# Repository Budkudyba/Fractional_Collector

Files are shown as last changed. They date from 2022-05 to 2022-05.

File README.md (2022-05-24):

# Fractional_Collector
## A Device that collects samples at interval.
A novel spin on fractional collection...Maintaining a Constant volume of the sampled media.  
  
The controller uses the Ramps 1.4 board and Arduino Mega commonly used in 3D printers. 
DRV8825 Stepper Drivers were used.  
  
The sampler takes samples based upon polling an added RTC (real-time clock).  
  
The sampler has two attached parastaltic pumps with stepper motors and a sample tray which is also powered by a stepper motor.  
The sample tray has room for 64 small eppendorf (1.5 mL).  
  
Here's a version of the sampler to show the basic form:  
fractional_collector_FINAL_SHOW
  
https://a360.co/2QkRquD

Libraries used:  
https://github.com/adafruit/RTClib  
https://github.com/olikraus/u8g2  
https://github.com/laurb9/StepperDriver

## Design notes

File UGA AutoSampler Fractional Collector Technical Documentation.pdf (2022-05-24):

## Constant Volume Fractional Collector 1.0

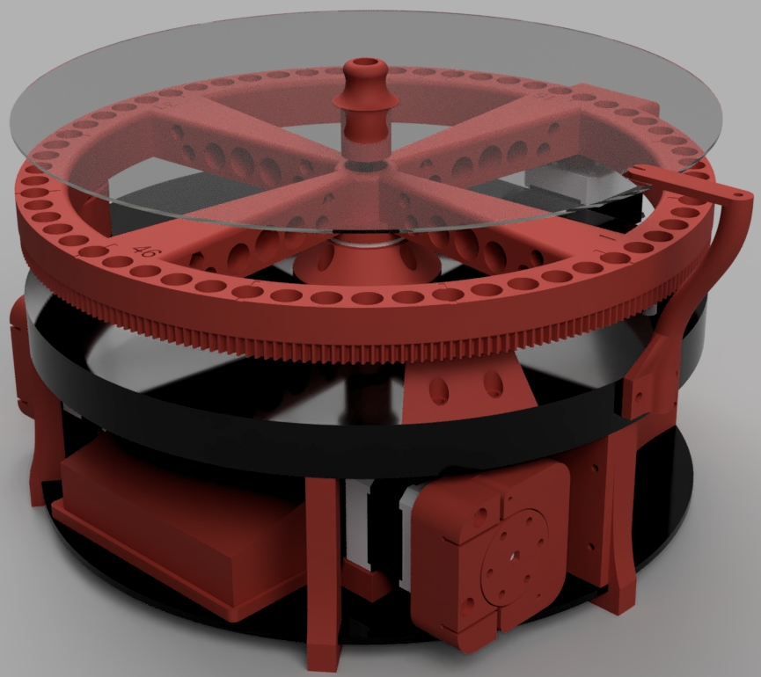
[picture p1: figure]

By: Paul Kudyba, III
8/30/18

### General Operation

- Description of Operation
- This device is used to sample at user given intervals from a blood bag or other sample container while keeping constant volume in the sample container. It can also be used to fill or empty a container to a set amount. Before each sample it will purge the dead volume from the sample tubing ensuring that samples taken are discrete. The controller interface is an LCD display with rotary encoder and push button for ease of operation.
- Powering the device
- The device is powered by a 12v power brick. USB is provided for updating the firmware only.
- Loading sample tubes
- With the top cover removed, place the tubes with the top facing outwards. If desired, you can alternate whether the top is facing inside or outside to help keep track of purge and sample tubes. If the mast is blocking the tube you would like to load/unload, then use the Tray Advance function.
- Purge and Sample
- The device will first purge and then sample. Therefore, each sample will be in an even numbered location.
- Menu Options
- Start
■ When all options are set. Depress the Knob to start the sampling operation. There is a delay of 15 seconds to provide time if an error in setup is made.
- Reset Total Samples
■ This is used to reset the number of samples back to zero. This will set both run and total sample counts back to zero. When used the machine will rehome and start from the first sample tray effectively starting over.
- Tray Advance
■ When loading/unloading, you may need to retrieve an eppendorf that is currently under the mast or move the tray to make it easier to load/unload. This moves the tray one position.
■ If used during a pause. It will resume where it left off after it rehomes. (Ex after taking 5 samples, you pause and advance the tray. When you resume it will resume taking sample 6 where sample 6 is normally taken.)
- Fill Bag
■ This fills the bag to a set amount. This can be changed with Set Bag Volume.
- Empty Bag
■ This empties the bag the amount set. This can be changed with Set Bag Volume.

- Set Cycle Interval
■ This sets how often samples are to be taken
- Set Sample Volume
■ This sets how much you would like to sample
- Set Purge Volume
■ This sets how much is needed to clear the dead volume within the tubing, needle tip, and IV spike. (0.5mL being plenty for up to 4ft of tubing)
- Set Bag Volume
■ This set how much will be pumped in the fill bag and empty bag function.
- Set Sample Limit
■ This is used to take a set number of samples and then pause. The number is taken from the total samples taken number not the run number. (ex. for 10 samples per run this needs to be set to 10 for run one, then 20 and then 30 in between each run)
- Calibrate Input Pump
■ This runs a calibration routine. It will pump a set amount and ask for a measurement of this amount to calculate the difference and adjust for any deviation. For the input pump it is 90mL. This will take a few minutes to pump.
- Calibrate Sample Pump
■ This runs a calibration routine. It will pump a set amount and ask for a measurement of this amount to calculate the difference and adjust for any deviation. For the input pump it is 8mL. This will take a few minutes to pump.
- Set Clock Time
■ This allows for setting/adjusting of the clock.
- Stats
■ This will display total cycles run by each pump. This will help indicate current wear of the tubing. This is not persistent across power cycles. To reset simply power cycle the machine.

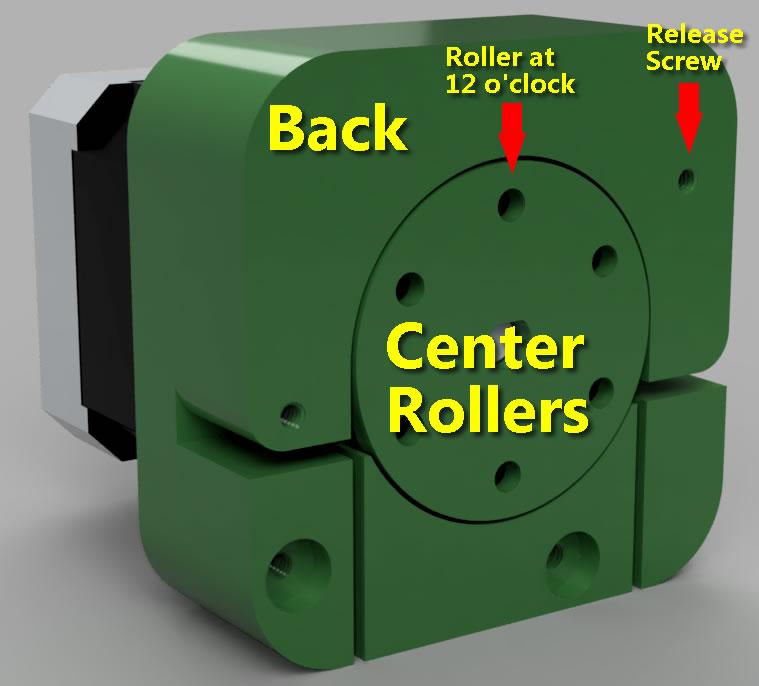
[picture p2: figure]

Changing the tubing

1. Find the release screw, and unscrew until the back of the pump can rotate out.
2. Remove and replace the tubing with the same size tubing required.
3. Close the back of the pump making sure the tubing is pulled taught and in the center of the channel. This is critical for the smaller sample pump.
4. While holding the pump closed so that the back is flat with the rest of the pump, tighten the screw. Do not continue to tighten if the screw is not seating in place.
5. Ensure that the hose is properly seated by:
a. On the larger (Input) pump pull on one side of the hose until you can see that it is drawing the other side into the pump.
b. On the smaller pump, pull until taught on both sides. Do not pull too hard or you may damage the small tubing.
6. Rotate the center rollers counter-clockwise until one of the rollers is at the twelve o’clock position. This ensures that you’ve not pinched the hose or have a bind in the pump. Having a roller at the 12 o’clock position ensures that no fluid will pass through the pump while at rest. This is where the roller “pinches” the hose.
7. Your pump is now ready for calibration.

### Troubleshooting

- Under normal operation the pumps and tray will be powered off when not active and thus able to be moved manually. If you bump the tray in between sampling you can simply pause and use the tray advance function. It will rehome and continue from where you left off when you resume sampling.
- If the pumps are not at the 12 o’clock position then the pumps may not function as intended.
- To first prime the input pump you can run the Fill Bag routine. You can set the volume you wish to prime with Set Bag Volume. When the pump is primed you can unplug the machine, but will lose any calibrations! or wait for the routine to finish. Priming the sample pump is unnecessary due to the purge function.
- Calibration is currently stored in volatile memory and therefore is lost when power is cut. If the device loses power then it must be calibrated before samping is resumed.
- If the sample limit (Set Sample Limit) is reached then it must be increased or the total samples reset (Reset Total Samples) otherwise the device will just pause again when told to sample due to its limit being reached.

### Silicone tubing Specifications

Sample Pump: 1.5mm OD, 0.5mm ID Input Pump: 4mm OD, 2mm ID

### Needle tip

Blunt 22 gauge at least 0.5in

### Eppendorf Specifications

1.5mL capacity micro centrifuge tubes

### Default Pump Calibrations

Input pump: 39.3095uL per ⅙ rotation sample pump: 2.20239uL per ⅙ rotation

### BOM Link

https://docs.google.com/spreadsheets/d/1MYYxMttSNWKxErDTZDmeEtySJJO_4VXljwuw_aIDuVE/edit?usp=sharing (https://docs.google.com/spreadsheets/d/1MYYxMttSNWKxErDTZDmeEtySJJO_4VXljwuw_aIDuVE/edit?usp=sharing)

### Firmware Code

https://drive.google.com/file/d/1aw9PEniRBlol2bpzdIY7CREgvx_vjx7f/view?usp=sharing

### STL Files (Pumps and Fractional Collector)

https://drive.google.com/file/d/1LXug6uyhkMV_s8yWWPx-mD0cbzlMRUWw/view?usp=sharing

### STL Files (IV Bag Adapters)

https://drive.google.com/file/d/1MMP1FGXNb9iqxeFYemUpdmFmI8zt_3Np/view?usp=sharing

### Assembly Drawings

https://drive.google.com/file/d/1KUkplYkBTQmoT0WgEx9ByRFT1yGoU6eH/view?usp=sharing

### Dead Volume Calculations

https://docs.google.com/spreadsheets/d/1AhHszSA9m7Kb7Sqf_vfh5iA0tXgWszb41xrvR_gTXpM/edit?usp=sharing (https://docs.google.com/spreadsheets/d/1AhHszSA9m7Kb7Sqf_vfh5iA0tXgWszb41xrvR_gTXpM/edit?usp=sharing)

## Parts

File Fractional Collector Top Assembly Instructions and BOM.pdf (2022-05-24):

# Fractional Collector Top Assembly Instructions and BOM

STL Link:
https://drive.google.com/file/d/1_8GxYKEukr-SobEUdoyhmjx0G93fVQS1/view?usp=sharing

# BOM

- 3D printed top in polycarbonate or other material able to be autoclaved.
- 22 gauge syringe needle 1½” (only for 2 port tops)
- ⅛” 304 Stainless Steel Tubing Precision (0.125" OD, 0.015" Wall Thickness)
- https://www.mcmaster.com/6100K491/
- #117 Hi-temp Silicone o-ring (red)

# Assembly Instructions

1. Cut 1/8" stainless tube to 1.5" long sections (dremel)
a. Deburr and polish (3/16" drill bit fits the ID)
2. Remove the needles point if hypodermic (dremel)
a. Cut needle tip from luer lock (dremel)
b. Very carefully deburr and polish (0.4mm drill bit fits the ID)
3. Drill top to size. (1/8" drill bit) (press fit)
4. Drill top to size. (0.8mm drill bit) (loose fit) (if required)
a. Press fit stainless tube into top till flush with thread bottom
b. Fit needle into top till flush with bottom (if required)
5. Prep 2 part epoxy (1 hr set is recommended)
a. Line epoxy around the needle and stainless tube
b. Ensure that it covers at least ⅛” up side of needle and stainless tube and ⅛” surrounding top to ensure good bond and proper seal
6. After allowing 24 hrs to cure place o-ring and it is ready for use

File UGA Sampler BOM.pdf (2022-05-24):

Constant Volume Fractional Collector BOM

Name of Part | Number | Price | Origin | Discription | Link | Price Per Unit
Ramps 1.4 Kit | 1 | $29.99 Ebay | https://www.ebay.com/itm/3D-Printer-Kit-Ramps-1-4-Mega2560-DRV8825-12864-LCD-for-Arduino-RepRap-USA/392055803590?ssPageName=STRK%3AMEBIDX%3AIT&_trksid=p2057872.m2749.l2649
Nema 17 Stepper Motors | 3 | $38.97 Amazon | https://www.amazon.com/gp/product/B00PNEQI7W/ref=oh_aui_search_detailpage?ie=UTF8&psc=1 $12.99
DS3231 Precision RTC | 1 | $2.35 Ebay | Real Time Clock | https://www.ebay.com/itm/DS3231-AT24C32-IIC-Precision-Real-Time-Clock-RTC-Memory-Module-for-Arduino/121936579559?ssPageName=STRK%3AMEBIDX%3AIT&_trksid=p2057872.m2749.l2649
LIR2032 Battery | 1 | $7.08 Ebay
| | | | DO NOT USE
CR2032 | https://www.ebay.com/itm/8-X-LIR2032-CR2032-2032-Top-Quality-Bulk-3-6V-Rechargeable-Lithium-Battery/142570686578?ssPageName=STRK%3AMEBIDX%3AIT&_trksid=p2057872.m2749.l2649
#4-40 Machine Screw x 3/4" | 8 | $0.47 Fastenal | https://www.fastenal.com/products/details/72490 $0.06

#4-40 Machine Screw x 1/2" | 20 | $0.60 Fastenal | https://www.fastenal.com/products/details/28655 $0.03

#4-40 Machine Screw x 1/4" | 8 | $0.24 Fastenal | https://www.fastenal.com/products/details/28631 $0.03

#4-40 Nut | 15 | $0.00 Fastenal

#6 Woodscrew Pan Head x 3/4" | 18 | $1.25 | https://www.fastenal.com/products/details/30562 $0.07

#10-24 Machine Screw x 1/2" | 1 | $0.04 Fastenal | https://www.fastenal.com/products/details/28957 $0.04

M3-0.5 x 6mm Machine Screw | 12 | $0.59 Fastenal
| | | | used to attach
stepper motors | https://www.fastenal.com/products/details/QM2510006A20000 $0.05
M3-0.5 x 10mm Machine Screw | 2 | $0.10 Fastenal | to secure endstop | https://www.fastenal.com/products/details/QM2510010A20000 $0.05
M5-0.8 x 50mm Machine Screw | 1 | $0.50 Fastenal | https://www.fastenal.com/products/details/QM2540050A20000 $0.50
M5-0.8 Nut | 2 | $0.24 Fastenal | https://www.fastenal.com/products/details/MN2540000A40000 0.12
Silicone Tubing 0.5mm x 1.5mm | >2ft | $11.26 Ebay | https://www.ebay.com/itm/ID-0-5x-OD-1-5mm-Silicone-Tubing-Food-Grade-Translucent-Rubber-Hose-Beer-Pipe-5M/302738630251?ssPageName=STRK%3AMEBIDX%3AIT&_trksid=p2057872.m2749.l2649
Silicone Tubing 2mm x 4mm | >2ft | $6.30 Amazon | https://www.amazon.com/gp/product/B01C3GCZTM/ref=oh_aui_detailpage_o09_s00?ie=UTF8&psc=1
1/8" x 3/4" Steel Dowel Pins x100 | 1 | $10.25 Ebay | 6 per pump | https://www.ebay.com/itm/1-8-X-3-4-Dowel-Pins-Hardened-Ground-1144-Grade-Steel-USA-Qty-100/173311906972?ssPageName=STRK%3AMEBIDX%3AIT&_trksid=p2057872.m2749.l2649
1kg PLA Filament | 1 | $22.99 Amazon | https://www.amazon.com/gp/product/B00J0EE1D4/ref=od_aui_detailpages00?ie=UTF8&psc=1
3/4" MDF | 1 | $7.71 Home Depot | https://www.homedepot.com/p/3-4-in-x-2-ft-x-2-ft-Medium-Density-Fiber-Board-1508111/205881912
1/4" Smooth Wood Paneling | 1 | $7.75 Home Depot | https://www.homedepot.com/p/Columbia-Forest-Products-1-4-in-x-2-ft-x-2-ft-PureBond-Pre-Primed-Poplar-Plywood-Project-Panel-Free-Custom-Cut-Available-3141/204940167?cm_mmc=Shopping%7CG%7CBase%7CD21%7C21-3_DIMENSIONAL_LUMBER%7CGeneric%7CPLA%7c71700000032182435%7c58700003832328702%7c92700036298154525&gclid=CjwKCAjwq57cBRBYEiwAdpx0vQEbKH0jGUsqRD1It-POHEHfkeOmMzfJ6ZSWmqfee-WHdmYR4G_bkhoCCkIQAvD_BwE&gclsrc=aw.ds&dclid=CKme2Papld0CFTbI4wcd2UMKgg
625ZZ | 2 | $1.40 Amazon | 5mm ID 16mm OD https://www.amazon.com/Bearing-Shielded-Miniature-Bearings-Skateboard/dp/B07DZDZNJM/ref=sr_1_2_sspa?ie=UTF8&qid=1535650890&sr=8-2-spons&keywords=625zz+bearing&psc=1 $0.70
Nylon Washer 1.25" x 0.38" x 0.125" | 2 | $1.90 Ace hardware | $0.95
Blunt 22g Needle | 1 | $0.38 Tractor Supply | Blunted with dremel https://www.tractorsupply.com/tsc/product/producers-pride-disposable-needle-22g-x-1-pack-of-6?cm_vc=-10005 $0.38
Total: | $151.98

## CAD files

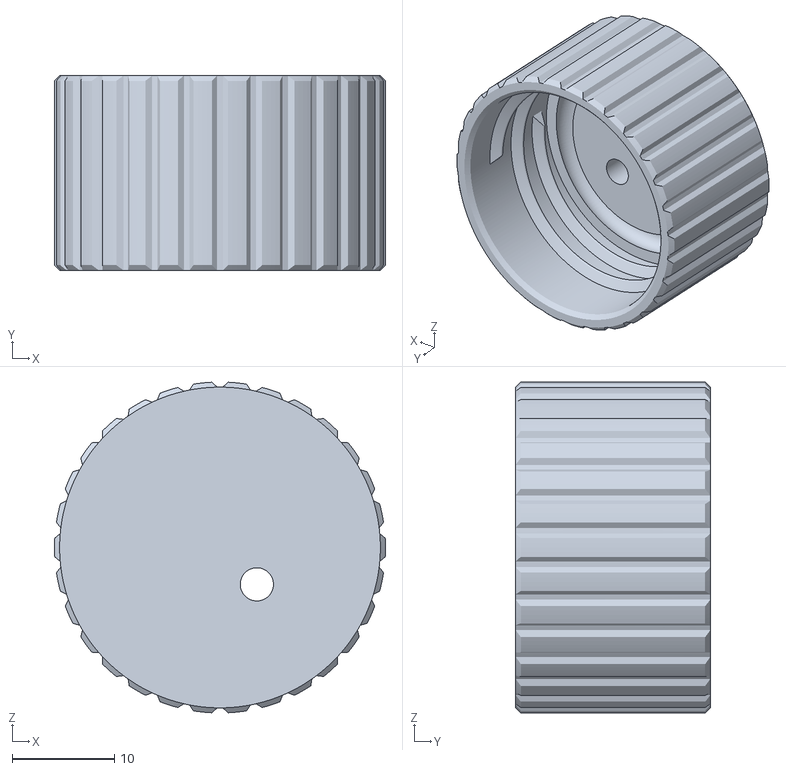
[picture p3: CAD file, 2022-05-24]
STL Files/Bottle Cap Flask FDM with barbs oring v5/Bottle Cap Flask FDM with barbs oring v5 Single.stl
32.3 x 19.0 x 32.3

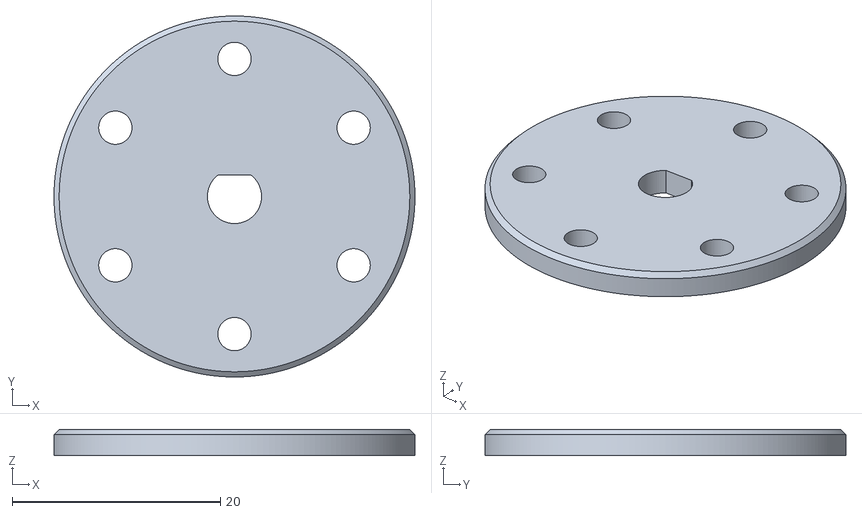
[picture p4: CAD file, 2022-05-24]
STL Files/input pump/roller_base.stl
34.7 x 34.7 x 2.50

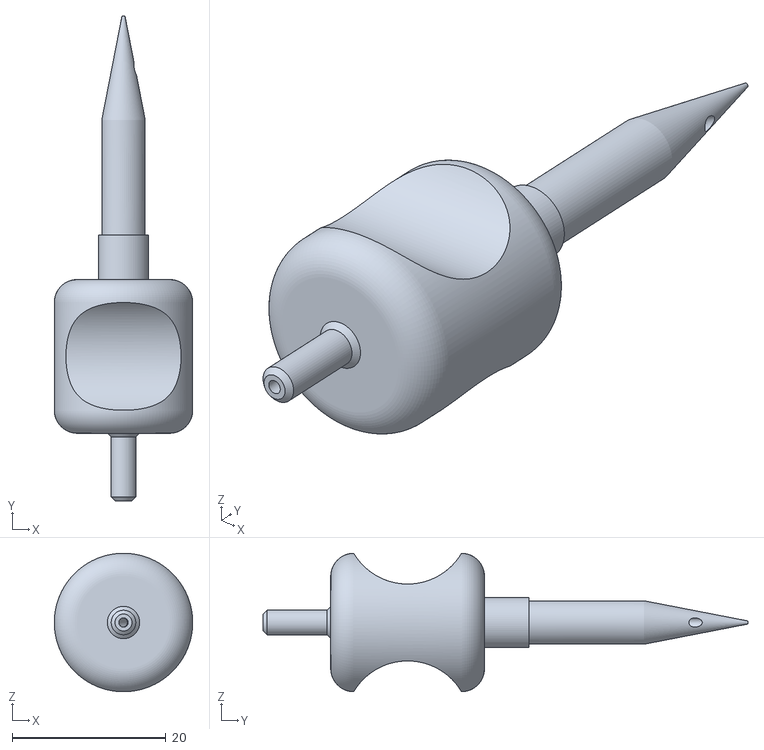
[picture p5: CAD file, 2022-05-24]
STL Files/IV Bag/iv spike to 2mm barb.stl
18.0 x 63.0 x 18.0

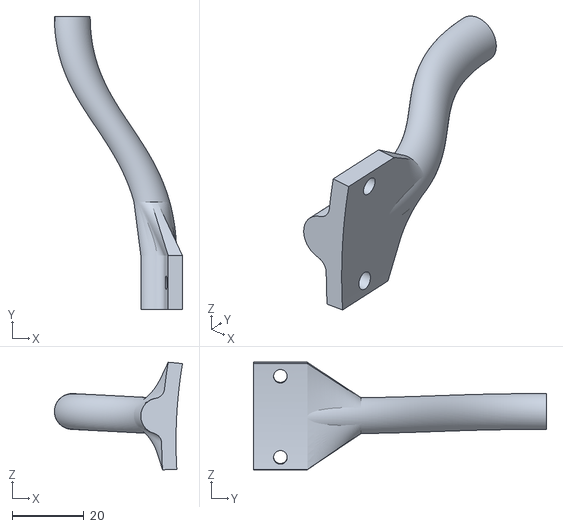
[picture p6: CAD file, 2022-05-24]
STL Files/mast.stl
35.7 x 81.7 x 30.0

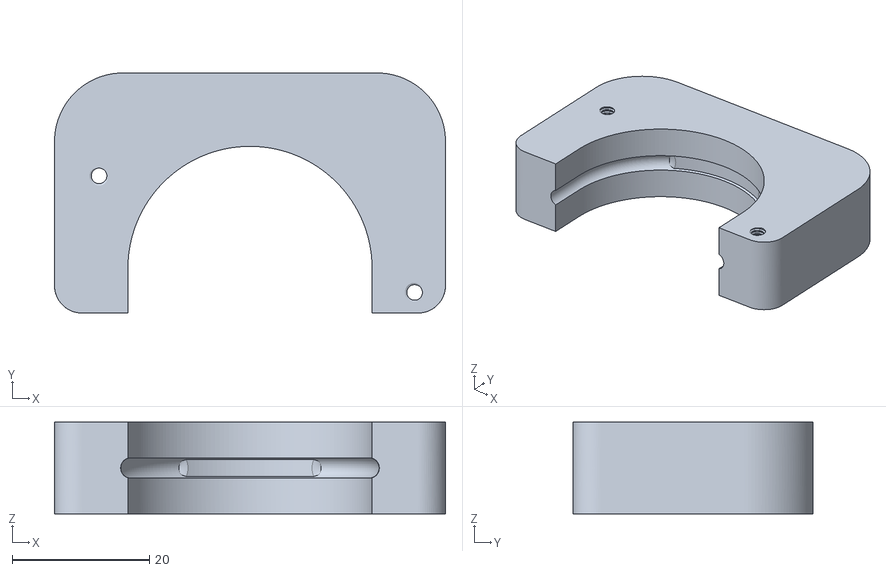
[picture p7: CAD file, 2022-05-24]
STL Files/sample pump/rider.stl
57.0 x 35.0 x 13.4

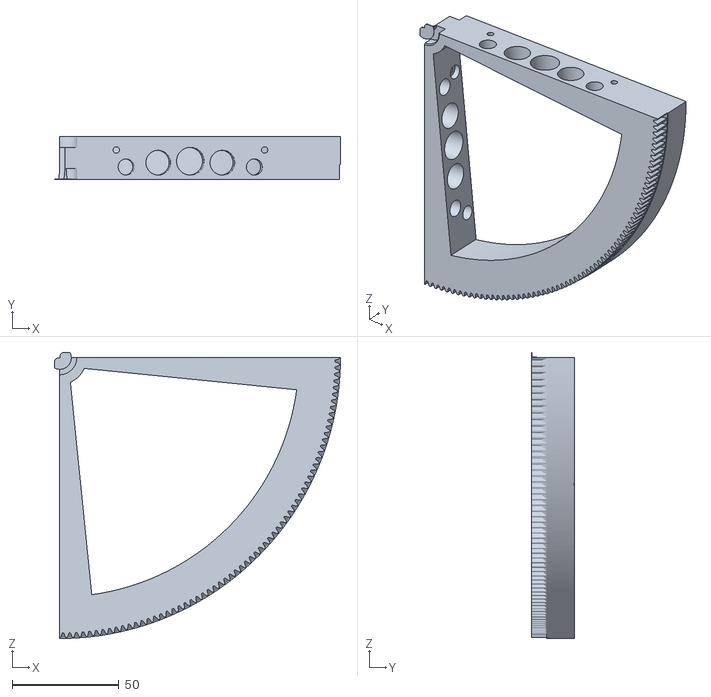
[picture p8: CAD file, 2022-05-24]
STL Files/fractional_collector_round 46.stl
133.8 x 20.0 x 133.8

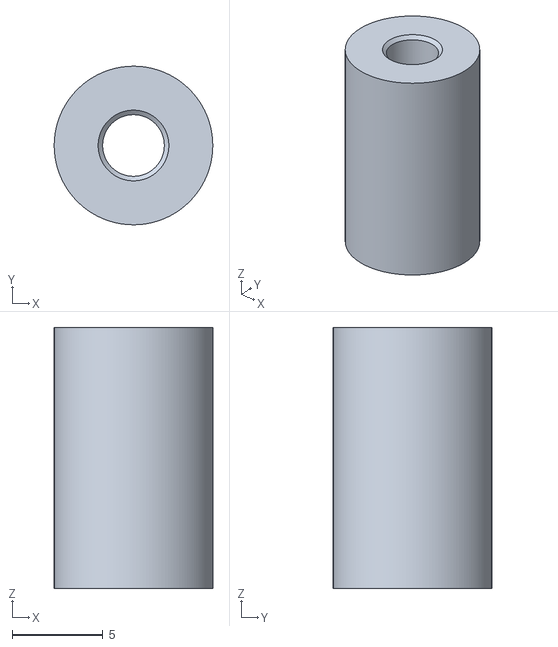
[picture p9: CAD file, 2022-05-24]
STL Files/input pump/roller.stl
8.75 x 8.75 x 14.4

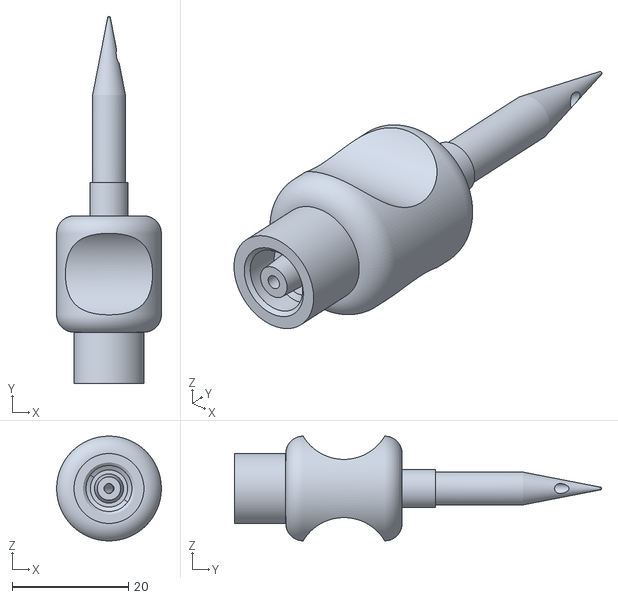
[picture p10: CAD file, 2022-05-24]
STL Files/IV Bag/iv spike to luer.stl
18.0 x 63.0 x 18.0

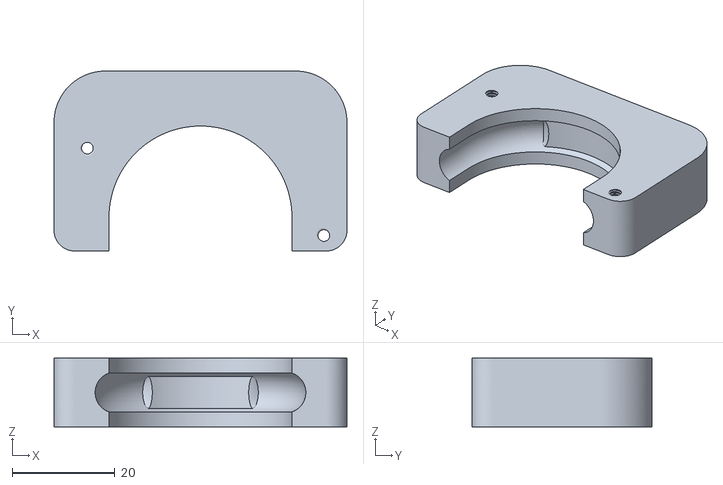
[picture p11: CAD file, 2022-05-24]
STL Files/input pump/rider.stl
57.0 x 35.0 x 13.4

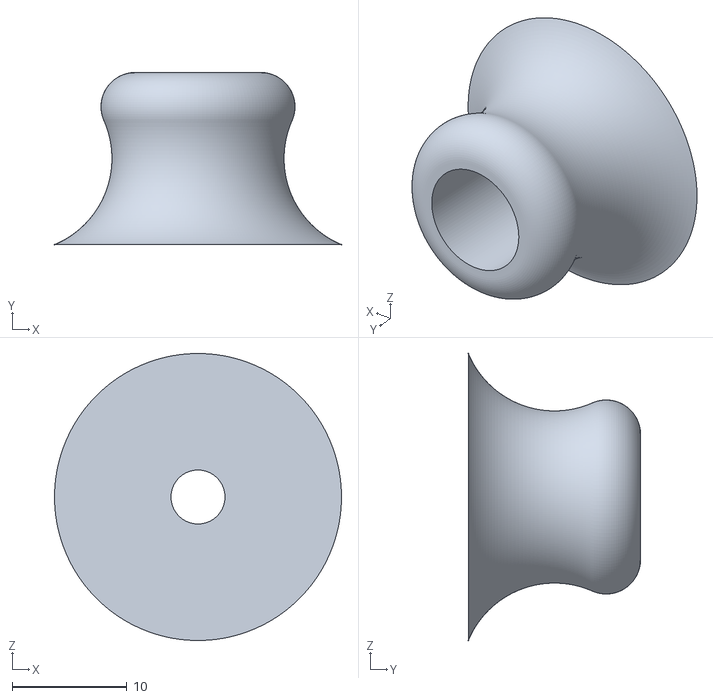
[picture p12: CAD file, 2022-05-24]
STL Files/lid_grip_top.stl
25.0 x 15.0 x 25.0

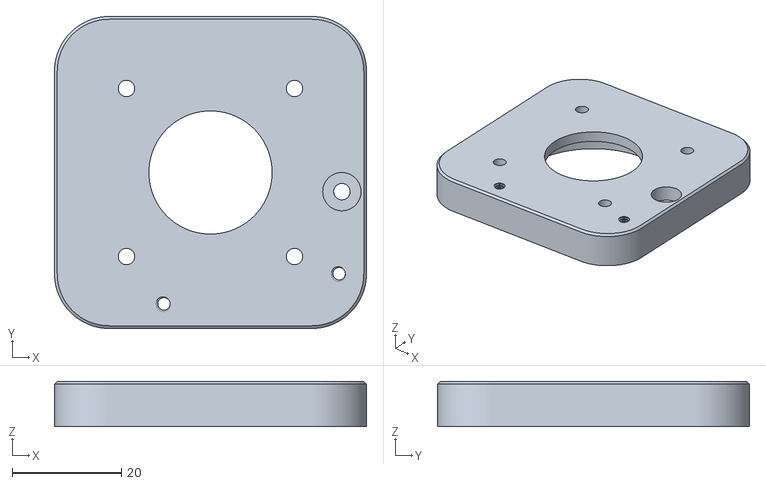
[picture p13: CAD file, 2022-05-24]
STL Files/input pump/base.stl
57.0 x 57.0 x 8.25

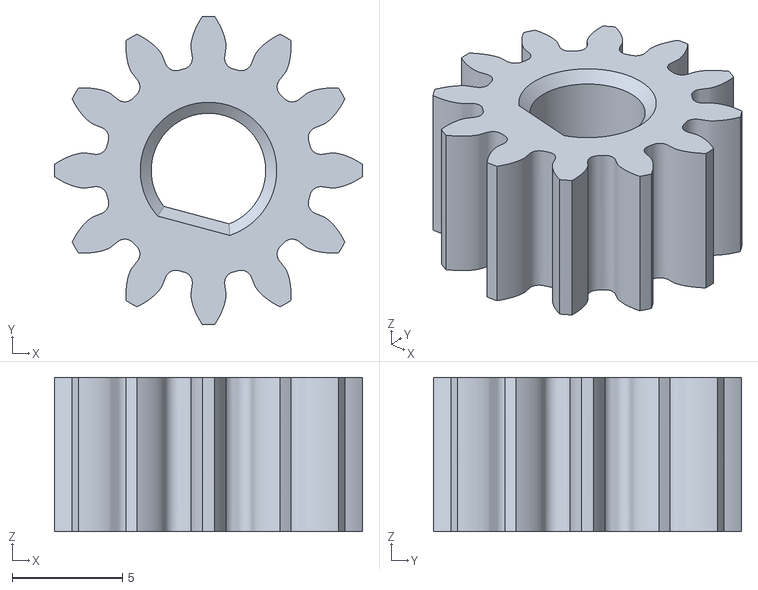
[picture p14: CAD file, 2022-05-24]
STL Files/motor_spur_gear.stl
14.0 x 14.0 x 7.00

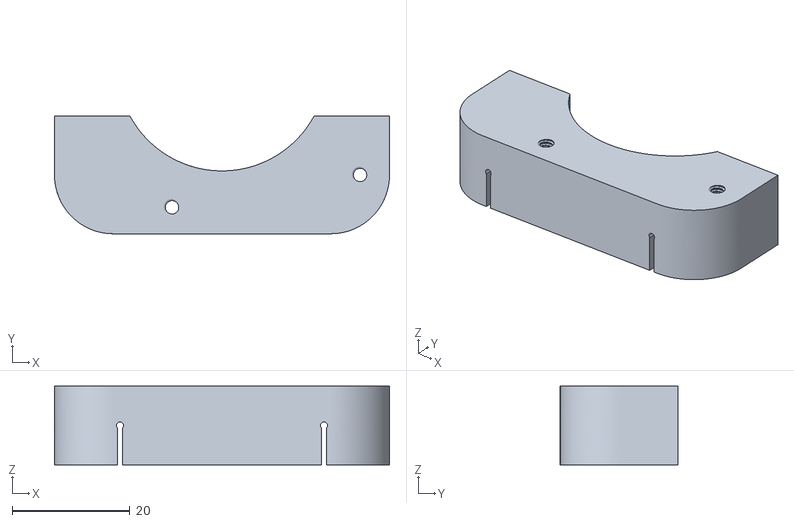
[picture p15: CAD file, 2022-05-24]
STL Files/sample pump/hose_grip.stl
57.0 x 20.0 x 13.4

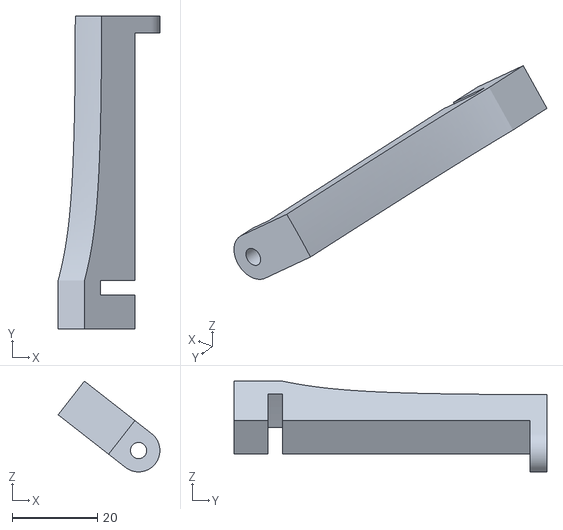
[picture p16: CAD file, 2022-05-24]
STL Files/front_bottom_spacer.stl
23.8 x 73.3 x 21.3

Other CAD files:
STL Files/Bottle Cap Flask FDM with barbs oring v5/Bottle Cap Flask FDM with barbs oring v5 Double.stl
STL Files/sample pump/roller.stl
STL Files/sample pump/roller_base.stl
STL Files/input pump/hose_grip.stl
STL Files/back_bottom_spacer.stl
STL Files/back_bottom_spacer_foot.stl
STL Files/back_plate.stl
STL Files/bumper.stl
STL Files/controller_mount.stl
STL Files/fractional_collector_round 1.stl
STL Files/fractional_collector_round 16.stl
STL Files/fractional_collector_round 31.stl
STL Files/front_skirt.stl
STL Files/idle_bumper_mount.stl
STL Files/lid_grip_bottom.stl
STL Files/lid_mount.stl
STL Files/mast_arm.stl
STL Files/middle_bottom_spacer.stl
STL Files/motor_mount.stl
STL Files/motor_mount_cover.stl
STL Files/mount_base.stl
STL Files/nylon center ring.stl
STL Files/pump_mount.stl
STL Files/sample pump/base.stl
STL Files/side_skirt.stl

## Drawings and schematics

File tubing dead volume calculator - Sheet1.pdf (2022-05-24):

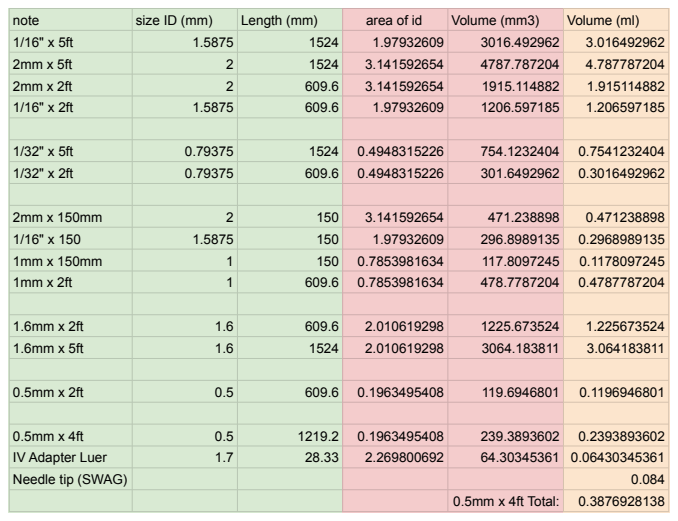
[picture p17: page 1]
note; size ID (mm); Length (mm); area of id; Volume (mm3); Volume (ml); IV Adapter Luer; Needle tip (SWAG); 0.5mm x 4ft Total:

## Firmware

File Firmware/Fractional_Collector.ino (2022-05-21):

//Created By: Paul Kudyba, III
// 8-17-20 version 1.6
//to be used with a Arduino MEGA, RAMPS 1.4 Board, and RepRapDiscount Controller

#define VERSION "1.6"

//LCD
#include <U8g2lib.h>
#include <SPI.h>
#include <Wire.h>
U8G2_ST7920_128X64_F_SW_SPI u8g2(U8G2_R0,23,17,16);//sck,mosi,cs

//encoder
static int pinA = 31;//encoder greycode clk
static int pinB = 33;//encoder greycode data
static int button = 35; //encoder button 
static int Estop = 41;//KILL_PIN 41 ?
int encoderPos = 0; 
//int encoderPinALast = LOW;
//int in = LOW;
static uint8_t prevNextCode = 0;
static uint16_t store=0;


//Home Switch
const int homeSwitch = 3; //X_MIN_PIN (can use interrupt)
bool HOMED = false;

// EEPROM
#include <EEPROM.h>
struct calibration {
  double uL2;
  double uL5;
  int set; //to see if EEPROM is valid is set to 43
  double sample;
  double purge;
  float interval;
};
calibration EEcal;//variable cal struct calibration to retrieve from eeprom

//RTC
#include <RTClib.h>
RTC_DS3231 rtc;

//Steppers
//#include "A4988.h" //changed to 8825
#include "DRV8825.h"
#define MOTOR_STEPS 200

//x axis (step, dir, en) (54,55,38)
//y axis (step, dir, en) (60,61,56)
//z axis (step, dir, en) (46,48,62)
//A4988 name(MOTOR_STEPS, DIR, STEP, ENABLE, MS1, MS2, MS3);
DRV8825 input(MOTOR_STEPS, 55, 54, 38); //x axis
DRV8825 output(MOTOR_STEPS, 61, 60, 56);//y axis
DRV8825 advance(MOTOR_STEPS, 48, 46, 62);//z axis
unsigned long totalMovedIn = 0;
unsigned long totalMovedOut = 0;
unsigned long totalMovedAd = 0;
int roundoffIn = 0; //used to align 200 steps to 1/6 rotations
int roundoffOut = 0;
double uL = 0; //volume difference from target
double uL2 = 39.3095; //default calibration 2mm dia pump
double uL5 = 2.20239; //default calibration 0.5mm dia pump
double cal = 0.0; // in mL used store amount to pump for calibration

//timers
unsigned long timer1 = 0;//used for encoder debounce
unsigned long timer2 = 0;//used for button encoder debounce
unsigned long debounce = 1;//5; //in ms
unsigned long buttonDebounce = 250; //in ms
unsigned long timer3 = 0;//used for rtc to trigger display update
unsigned long dispRTC = 1000; //in ms

//states, menu items, and variables
unsigned int state = 0;
int dispNeedsUpdate = 1;

double sample = 500;// in ul
double purge = 500;// in ul
float interval = 15.0; //in mins
DateTime startTime; // when to start
DateTime lastSampleTime;
int samplesTaken = 0; //total samples per experiment
int intervalSamples = 0; // samples taken without pause
DateTime nextInterval;
bool isClockSet = true;
bool powerLossWhileRunning = false;
int sampleLimit = 30;


//constants
const char States[16][20] = {"Start", "Reset Total Samples", "Tray Advance", "Start at Sample",
                            "Set Cycle Interval", "Set Sample Volume", "Set Purge Volume",
                            "Set Sample Limit",
                            "Cal. Input Pump", "Cal. Sample Pump",
                            "Set Clock Time", "Stats", "Sampler v"VERSION};

void setup() {
  //serial
  Serial.begin(115200);
  Serial.println("Welcome");
  Serial.println("Sampler v"VERSION);
  //LCD
  u8g2.begin();
  //Encoder and Pins
  pinMode(pinA, INPUT_PULLUP); 
  pinMode(pinB, INPUT_PULLUP);
  pinMode(button, INPUT_PULLUP);//active low
  pinMode(Estop, INPUT_PULLUP); //stop button on panel
  pinMode(homeSwitch, INPUT_PULLUP);
  
  //RTC
  rtc.begin();
  if (rtc.lostPower()){
    isClockSet = false;
    rtc.adjust(DateTime(2018, 7, 21, 0, 0, 55));
  }
  //Steppers
  input.begin(120);//120RPM
  input.disable();
  input.setMicrostep(8);
  output.begin(120);
  output.disable();
  output.setMicrostep(8);
  advance.begin(60);
  advance.disable();
  advance.setMicrostep(8);
  advance.setSpeedProfile(advance.LINEAR_SPEED, 2000, 1000);// enable accel,decel
  
  //Welcome Screen
  u8g2.clearBuffer();
  u8g2.setFont(u8g2_font_ncenB14_tr);
  u8g2.drawStr(14,30,"Welcome!");
  u8g2.sendBuffer();
  delay(2000);
  u8g2.setFont(u8g2_font_t0_12b_tf);
  
  //get calibrations from EEPROM
  Serial.println("Reading EEPROM");
  EEPROM.get(0, EEcal);//address,variable
  Serial.print("uL2: ");
  Serial.println(EEcal.uL2,5);
  Serial.print("uL5: ");
  Serial.println(EEcal.uL5,5);
  Serial.print("set: ");
  Serial.println(EEcal.set);
  Serial.print("sample: ");
  Serial.println(EEcal.sample,2);
  Serial.print("purge: ");
  Serial.println(EEcal.purge,2);
  Serial.print("interval: ");
  Serial.println(EEcal.interval,2);
  if(EEcal.set == 43) {//EEPROM has been written to before
    Serial.print("Loading from EEPROM...");
    uL2 = EEcal.uL2;
    uL5 = EEcal.uL5;
    sample = EEcal.sample;
    purge = EEcal.purge;
    interval = EEcal.interval;
    Serial.println("Success!");
  }
  if(EEcal.set != 43){//EEPROM has never been written to, and needs to be set
    Serial.println("EEPROM nan detected");
    Serial.println("Writing default values");
    EEcal.uL2 = uL2;
    EEcal.uL5 = uL5;
    EEcal.set = 43;
    EEcal.sample = sample;
    EEcal.purge = purge;
    EEcal.interval = interval;
    EEPROM.put(0,EEcal);
    Serial.println("Default values written");
  }
}

void loop() {
  if (millis() - timer1 > debounce){
    timer1 = millis();
    pollEncoder();
  }
  switch(state){
    case 0://------------------------------Start
      if (dispNeedsUpdate) {
        DateTime now = rtc.now();
        timer3 = millis(); //reset RTC timer
        u8g2.clearBuffer();
        u8g2.setCursor(2, 12);
        u8g2.print(States[state]);
        u8g2.setFont(u8g2_font_t0_11_tf);
        u8g2.setCursor(40, 15);
        String s = "Sample:";
        String ml = "mL";
        String t = s + sample/1000 + ml;
        u8g2.setCursor(45, 12);
        u8g2.print(t);
        String p = " Purge:";
        t = p + purge/1000 + ml;
        u8g2.setCursor(45, 22);
        u8g2.print(t);
        String q = "Every:";
        String mins = "mins";
        t = q + interval + mins;
        u8g2.setCursor(45, 31);
        u8g2.print(t);
        String col = ":";
        t = addLeadingZero(now.hour()) + col + addLeadingZero(now.minute()) + col + addLeadingZero(now.second());
        u8g2.setCursor(55, 64);
        u8g2.print(t);
        if (!isClockSet){
          u8g2.setCursor(2, 64);
          u8g2.print("SetClock!");
        }
        if (samplesTaken > 0){
          u8g2.setCursor(2, 53);
          String q = "Paused at Sample: ";
          t = q + addLeadingZero(samplesTaken);
          u8g2.print(t);      
        }
        u8g2.sendBuffer();
        u8g2.setFont(u8g2_font_t0_12b_tf);//reset font to default
        dispNeedsUpdate = 0;
      }
      if (encoderPos > 0){
        state++;
        encoderPos = 0;
        dispNeedsUpdate = 1;
        break;
      }
      if (!digitalRead(button) && millis() - timer2 > buttonDebounce){
        timer2 = millis();
        state = 50;//waiting
        dispNeedsUpdate = 1;
        startTime = rtc.now();
        nextInterval = startTime.unixtime() + long(15);
        //Serial.println(startTime.unixtime());
        //Serial.println(nextInterval.unixtime());
        break;
      }
      if (millis() - timer3 > dispRTC){ //update clock display
        dispNeedsUpdate = 1;
      }
    break;
    case 1://------------------------------RESET TOTAL SAMPLES
      if (dispNeedsUpdate) {
        u8g2.clearBuffer();
        u8g2.setCursor(2, 12);
        u8g2.print(States[state]);
        String s = "Total Samples: ";
        String t = s + addLeadingZero(samplesTaken);
        u8g2.setCursor(2, 50);
        u8g2.print(t);
        u8g2.sendBuffer();
        dispNeedsUpdate = 0;
      }
      checkEncoderMenuStatus();
      if (!digitalRead(button) && millis() - timer2 > buttonDebounce){
        timer2 = millis();
        samplesTaken = 0;
        intervalSamples = 0;
        HOMED = false;
        dispNeedsUpdate = 1;
      }
    break;
    case 2://------------------------------TRAY ADVANCE
      updateDisplay();
      checkEncoderMenuStatus();
      if (!digitalRead(button) && millis() - timer2 > buttonDebounce){
        timer2 = millis();
        HOMED = false;
        advance.enable();
        advance.move(-578);
        advance.disable();
        dispNeedsUpdate = 1;
      }
    break;
    case 3://------------------------------START AT SAMPLE
      updateDisplayWithUnits(samplesTaken, "");
      checkEncoderMenuStatus();
      samplesTaken = changeValueRehome(samplesTaken, 1, 0, 29, "");//value, increment, min, max, unit
    break;
    case 4://------------------------------SET CYCLE INTERVAL
      updateDisplayWithUnits(interval, "min");
      checkEncoderMenuStatus();
      interval = changeValue(interval, 1, 1, 120.0, "min");//value, increment, min, max, unit
      EEcal.interval = interval;
      EEPROM.put(0,EEcal);
    break;
    case 5://------------------------------SET SAMPLE VOLUME
      updateDisplayWithUnits(sample, "uL");
      checkEncoderMenuStatus();
      sample = changeValue(sample, 10, 20, 1500, "uL");//value, increment, min, max, unit
      EEcal.sample = sample;
      EEPROM.put(0,EEcal);
    break;
    case 6://------------------------------SET PURGE VOLUME
      updateDisplayWithUnits(purge, "uL");
      checkEncoderMenuStatus();
      purge = changeValue(purge, 10, 20, 1500, "uL");//value, increment, min, max, unit
      EEcal.purge = purge;
      EEPROM.put(0,EEcal);
    break;
    case 7://------------------------------SET SAMPLE LIMIT
      updateDisplayWithUnits(sampleLimit, "");
      checkEncoderMenuStatus();
      sampleLimit = changeValue(sampleLimit, 1, 1, 30, "");//value, increment, min, max, unit
    break;
    case 8://------------------------------CAL INPUT PUMP
      updateDisplay();
      checkEncoderMenuStatus();
      if (!digitalRead(button) && millis() - timer2 > buttonDebounce){
        timer2 = millis();
        dispNeedsUpdate = 1;
        cal = 90.0; // in mL
        int ini = 90000/uL2; //closest uL to target
        InMove6(ini, "Calibrate 90mL", uL2);
        do{
          if (!digitalRead(button) && millis() - timer2 > buttonDebounce){
            dispNeedsUpdate = 1;
            timer2 = millis();
            break;
          }
          pollEncoder();
          if (encoderPos!=0){
            cal+=float(encoderPos)*0.1;
            if (cal < 0){
              cal = 0;
            }
            dispNeedsUpdate = 1;
            encoderPos = 0;
          }
          updateDisplayWithUnitsEDIT(cal,"mL");
        }while(true); 
        uL2 = uL2 * cal * 1000 / 90000; //update calibration
        //Store calibration in EEPROM
        EEcal.uL2 = uL2;
        EEPROM.put(0,EEcal);
        //Serial.println(uL2);      
      }
    break;
    case 9://------------------------------CAL SAMPLE PUMP
      updateDisplay();
      checkEncoderMenuStatus();
      if (!digitalRead(button) && millis() - timer2 > buttonDebounce){
        timer2 = millis();
        dispNeedsUpdate = 1;
        cal = 8.0; // in mL
        int ini = 8000/uL5; //closest uL to target
        OutMove6(ini, "Calibrate 8mL", uL5);
        do{
          if (!digitalRead(button) && millis() - timer2 > buttonDebounce){
            dispNeedsUpdate = 1;
            timer2 = millis();
            break;
          }
          pollEncoder();
          if (encoderPos!=0){
            cal+=float(encoderPos)*0.1;
            if (cal < 0){
              cal = 0;
            }
            dispNeedsUpdate = 1;
            encoderPos = 0;
          }
          updateDisplayWithUnitsEDIT(cal,"mL");
        }while(true); 
        uL5 = uL5 * cal * 1000 / 8000; //update calibration
        EEcal.uL5 = uL5;
        EEPROM.put(0,EEcal);
        //Serial.println(uL5);      
      }
    break;
    case 10://------------------------------SET TIME
      if (dispNeedsUpdate) {
        DateTime now = rtc.now();
        timer3 = millis(); //reset RTC timer
        u8g2.clearBuffer();
        u8g2.setCursor(2, 12);
        u8g2.print(States[state]);
        u8g2.setFont(u8g2_font_courB08_tf);
        String col = ":";
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
